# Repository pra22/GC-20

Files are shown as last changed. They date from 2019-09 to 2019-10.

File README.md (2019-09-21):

# GC-20
### Portable Geiger counter, dosimeter and monitoring station with features such as:
- Touchscreen controlled, intuitive GUI
- Displays counts per minute, current dose, and accumulated dose on homescreen
- Sensitive and reliable SBM-20 Geiger-Muller tube
- Variable integration time for averaging dose rate
- Timed count mode for measuring low doses
- Choose between Sieverts and Rems as the units for the displayed dose rate
- User adjustable alert threshold
- Adjustable calibration to relate CPM to dose rate for various isotopes
- Audible clicker and LED indicator toggled on and off from homescreen
- Offline data logging
- Post bulk logged data to cloud service (ThingSpeak) to graph, analyze and/or save to computer
- Monitoring Station mode: device stays connected to WiFi and regularly posts ambient radiation level to ThingSpeak channel

### Overview and User's Guide

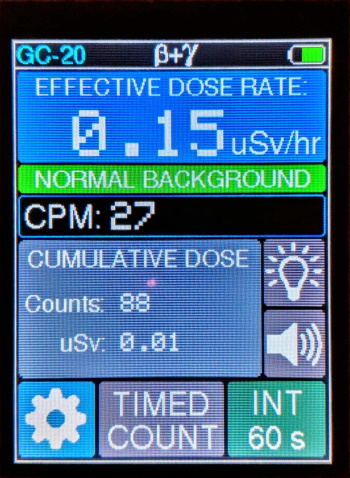
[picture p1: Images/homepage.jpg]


The homepage displays the current effective dose rate, counts per minute, and the cumulative dose since the device was turned on. The integration time can be changed by tapping the "INT 60 s" button and the user can choose between 60, 180 and 5 seconds of integration. A shorter time allows faster response to changing radiation levels at the expense of accuracy. Using 180 seconds gives the least amount random fluctuation.

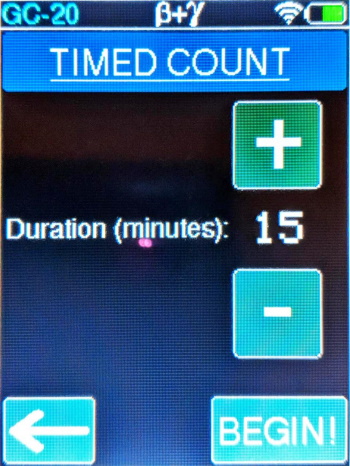
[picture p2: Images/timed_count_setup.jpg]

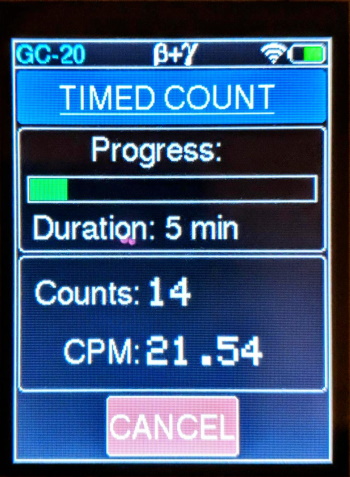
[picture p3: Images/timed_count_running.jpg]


The timed count mode allows for the measurement of very low doses of radiation such as the radiation coming from bananas, brazil nuts, or granite. It can also be used to test for high levels of Radon. Select the time interval in five minute increments, hit begin, and the GC-20 starts counting and displaying the accumulated counts over time. It also displays the real time CPM during the timed count. 
The WiFi symbol next to the battery level indicator means that the GC-20 is currently in monitoring station mode and is connected to WiFi. More on that below.

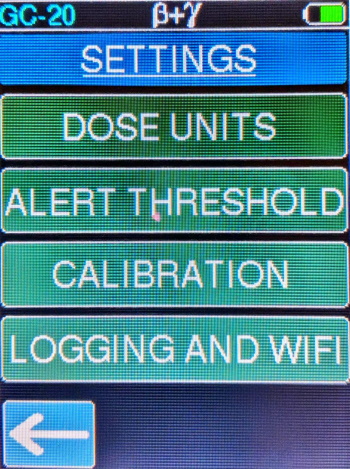
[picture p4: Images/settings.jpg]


The settings menu has four options: Dose Units, Alert Threshold, Calibration, and Logging and WiFi. 

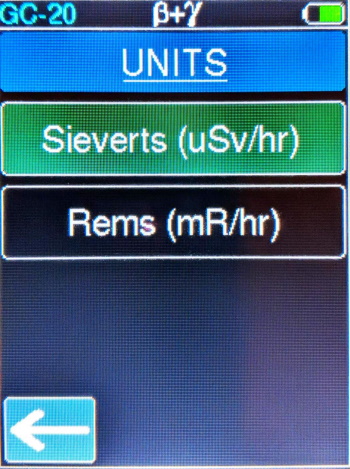
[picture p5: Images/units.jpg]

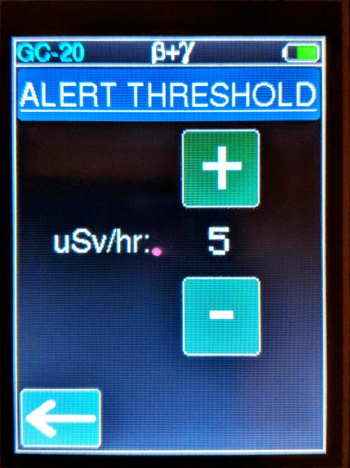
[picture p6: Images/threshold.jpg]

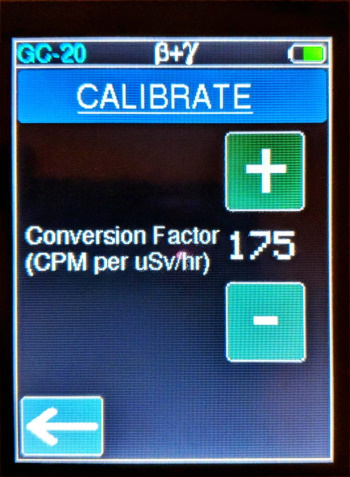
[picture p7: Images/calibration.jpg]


The Dose Units option allows the user to choose between either Sieverts or Rems for the effective dose rate and the accumulated dose.

The user can adjust the threshold at which the home page displays a "High Radiation Level" alert in red, in increments of 1 uSv/hr.

The calibration factor that relates CPM to uSv/hr can be changed using this option. The geiger tube has different sensitivities to different isotopes, so to keep the dose readings reasonably accurate, a default conversion factor of 175 is used. This will accurately report the gamma dose from Cesium-137. 

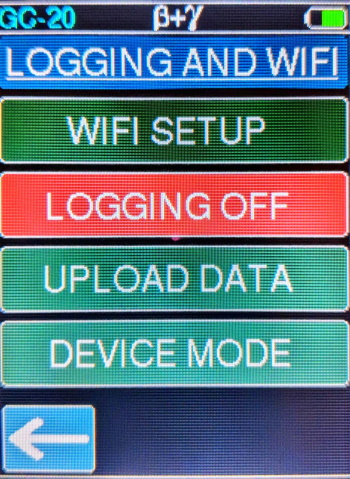
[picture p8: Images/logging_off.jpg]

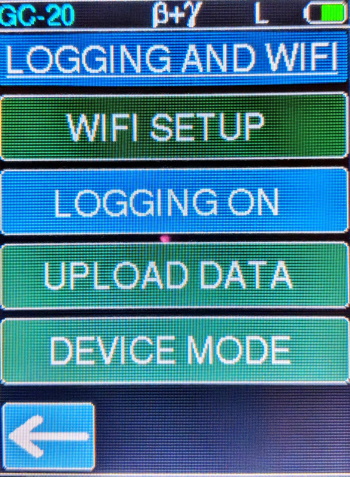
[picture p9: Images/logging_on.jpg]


Finally, tapping the Logging and WiFi button offers a further sub-menu of options related to setting up wifi for the first time, logging data, uploading logged data, and setting the device mode. When data logging is on, an "L" symbol appears on the top bar.

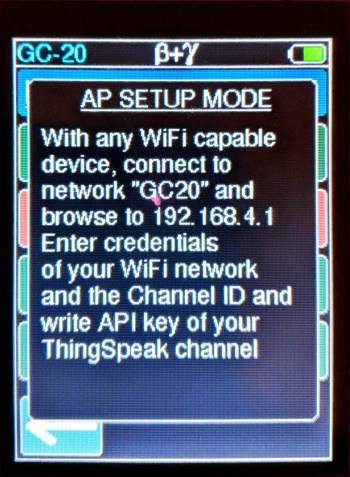
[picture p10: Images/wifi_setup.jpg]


To set up WiFi, tap on WiFi setup and the GC-20 will enter AP mode. Using any wifi connected device with a web browser, like a phone or a laptop, search local networks and connect to the open network named "GC20". The browser will either automatically take you to the setup page, or if doesn't, enter the url 192.168.4.1. Select your network name from the scanned list, enter the password, and also enter the credentials of your ThingSpeak channel, i.e. the channel ID and the write API. Once that's done, hit save and the GC-20 will save the settings to permanent memory and reset itself. You can always change the wifi or channel details at any time by repeating the above.

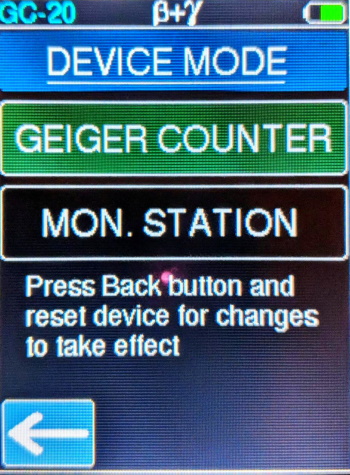
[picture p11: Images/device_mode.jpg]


In the Device Mode menu option, the user can choose between the portable Geiger counter mode, or configure the device as a radiation monitoring station. In the monitoring station mode, the GC-20 is always connected to WiFi, and updates the ThingSpeak field every 5 minutes. If it can't connect to WiFi during startup, it waits for 30 seconds before starting in portable Geiger counter mode.

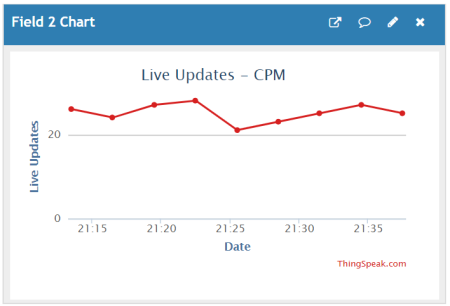
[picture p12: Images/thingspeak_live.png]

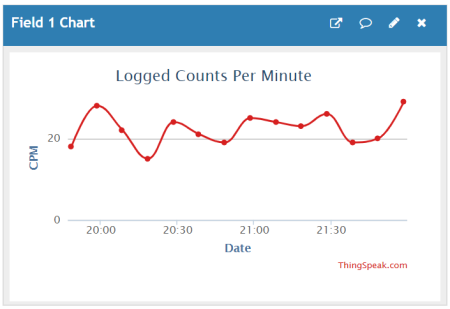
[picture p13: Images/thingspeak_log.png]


Examples of the ThingSpeak data plots from the radiation monitor and from a bulk-upload of logged data.

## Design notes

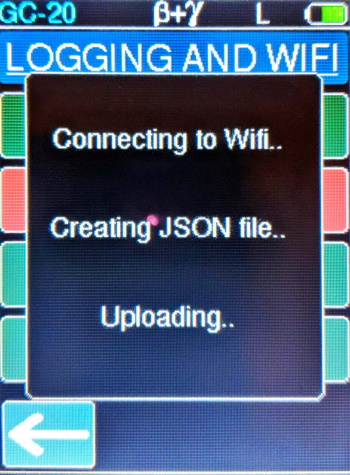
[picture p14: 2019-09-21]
Images/uploading.jpg

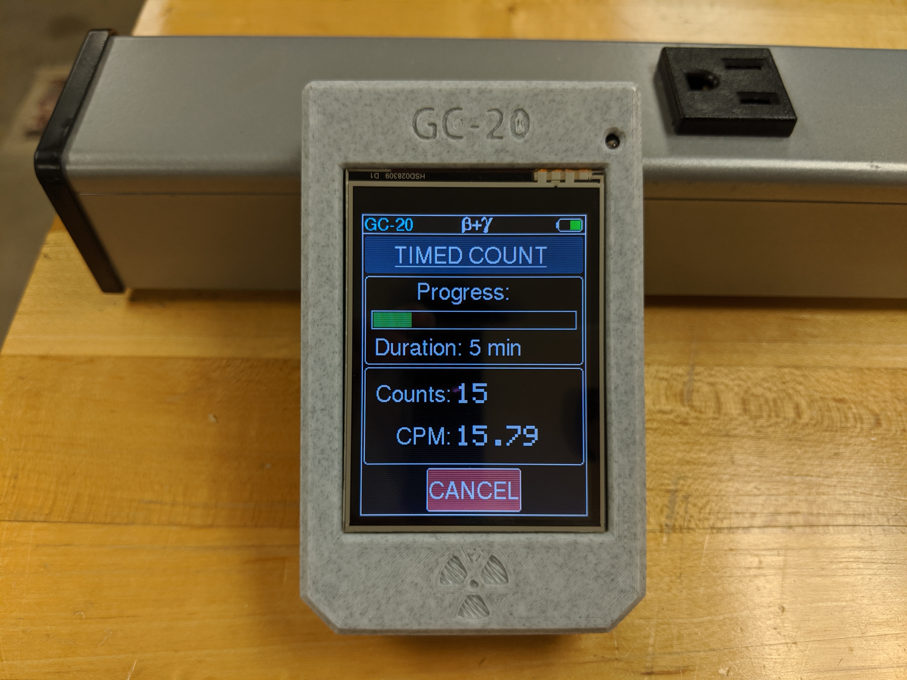
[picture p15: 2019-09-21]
Images/timedcount.jpg

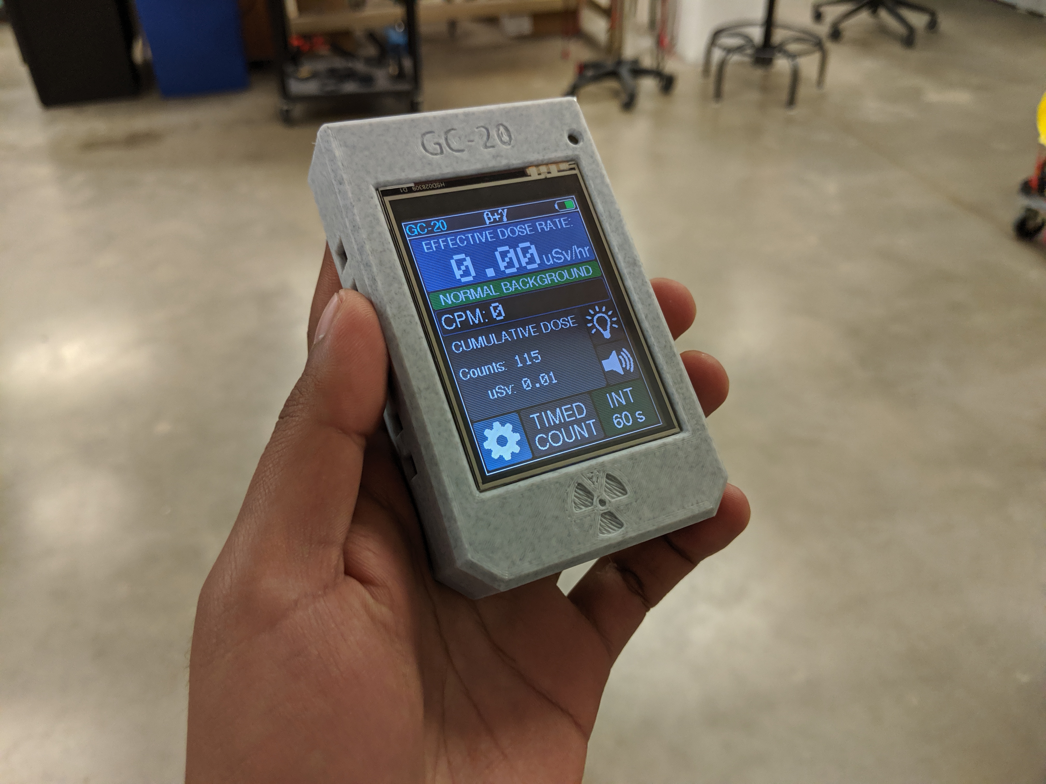
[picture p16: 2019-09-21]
Images/handheld4.jpg

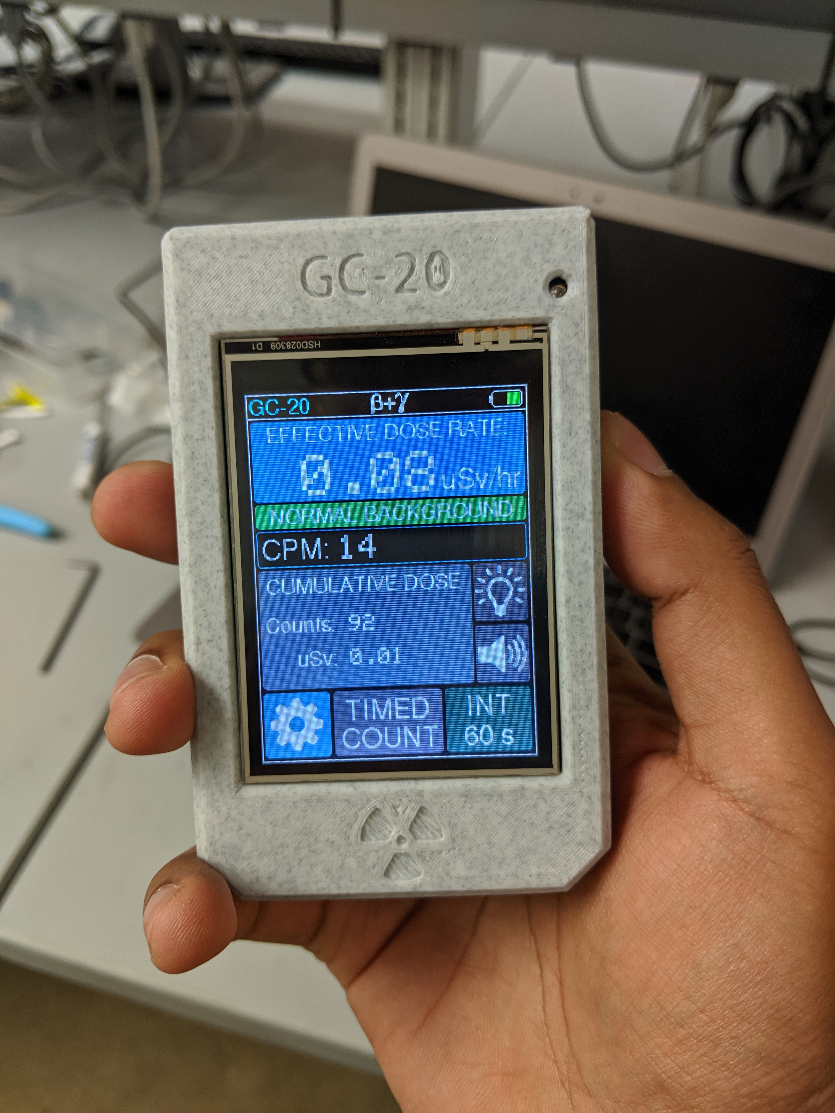
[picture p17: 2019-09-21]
Images/handheld3.jpg

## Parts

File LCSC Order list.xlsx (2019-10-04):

LCSC order information for electronic components for the GC-20
Reference Designator | Value/Description | LCSC Part Number | Footprint
U1 | CMOS 555 timer | C383061 | SOP-8
U5 | 3V LDO linear regulator | C98226 | SOT-89
C1 | 1 nF MLCC 50V | C1885 | 1206
C2 | 10 nF 1000V | C107192 | 1206
C3 | 220 pF MLCC 500V | C106036 | 1206
C4 | 10 uF Tantalum | C119050 | CASE-B_3528
C5 | 100 nF MLCC | C82601 | 1206
R1 | 100K | C17900 | 1206
R2 | 220K | C17956 | 1206
R3 | 330 | C104763 | 1206
R4 | 1K | C4410 | 1206
R5 | 100 Ohm Variable Resistor | C128542 | Custom
R6 | 4.7M | C37800 | 1206
R7 | 10K | C140407 | 1206
R8 | 100K | C17900 | 1206
R9 | 22K | C25830 | 1206
R10 | 220K | C17956 | 1206
R11 | 330 | C104763 | 1206
D1 | Fast recovery 600V diode | C183411 | SMAF
D2 | Fast recovery 600V diode | C183412 | SMAF
Q1 | NPN Transistor 200mA 400V | C181174 | SOT-23
Q2 | NPN Transistor 200mA 40V | C111113 | SOT-23
Q3 | NPN Transistor 200mA 40V | C111113 | SOT-23
Q4 | NPN Transistor 200mA 40V | C111113 | SOT-23
L1 | 10 mH Power Inductor | C168108 | Custom
BUZZER1 | Magnetic Buzzer | C189208 | 7.5*7.5*2.5mm
SW1 | Power switch SMD | C405951 | Custom
B1 | JST PH battery connector | C265016 | TH, 2mm pitch
LED1 | Red LED 3mm | C330752 | TH

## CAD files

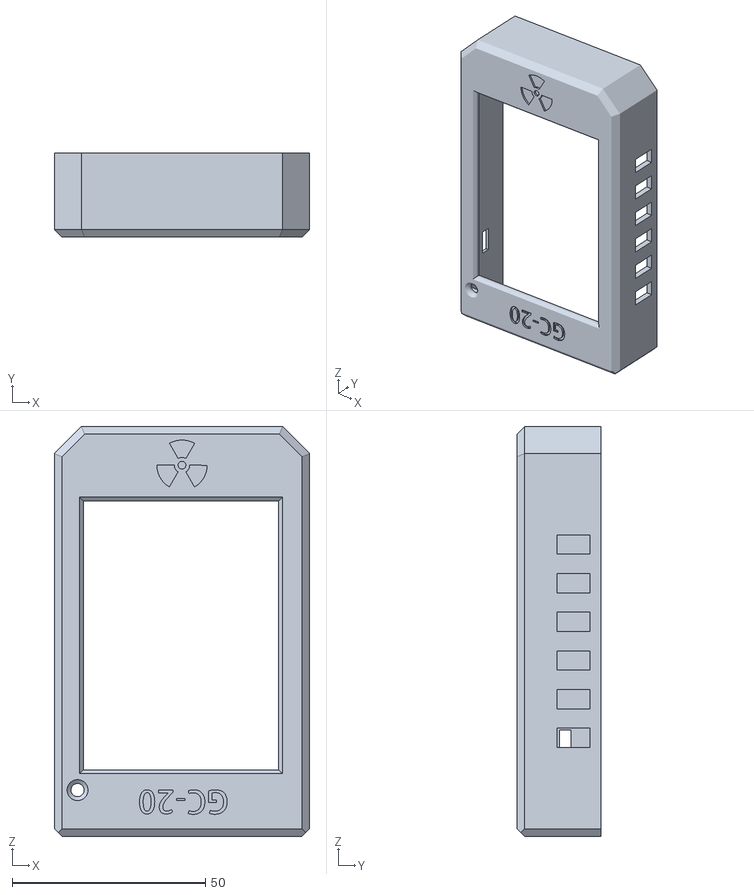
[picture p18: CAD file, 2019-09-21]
STL Files/Case main.STL
66.0 x 21.8 x 106.0

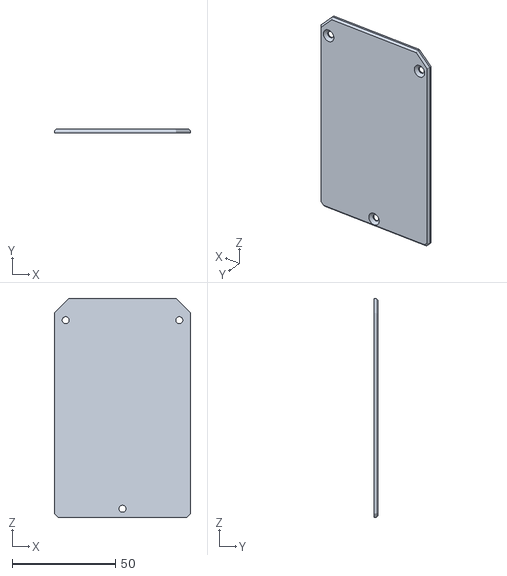
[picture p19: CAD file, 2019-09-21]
STL Files/Cover.STL
66.0 x 2.00 x 106.0

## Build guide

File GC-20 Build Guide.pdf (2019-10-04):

v1.1 | 10/04/2019

### GC-20 Geiger Counter, Dosimeter and Radiation Monitoring Station

Build Guide

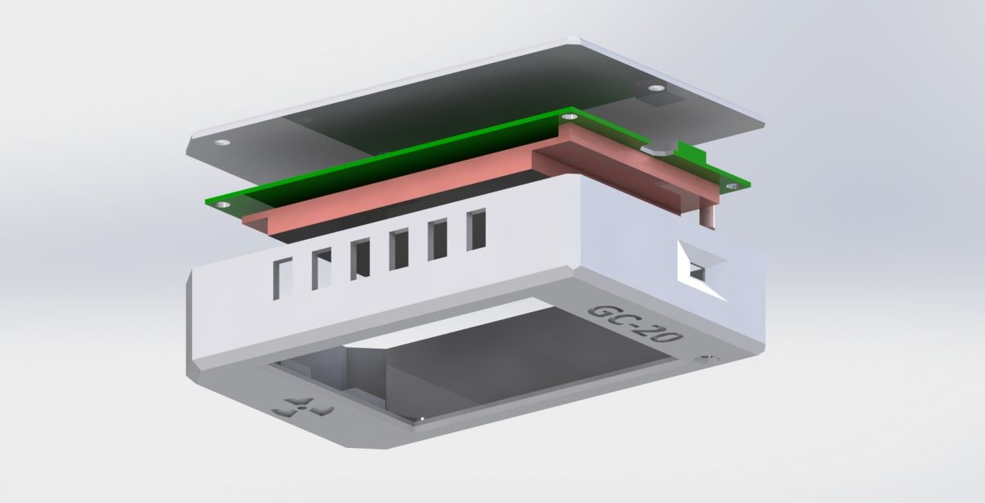
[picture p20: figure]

Figure 1: Rendering of the CAD model

All hardware design files for the GC-20 are available at my GitHub page at github.com/pra22/GC20. This includes the Solidworks CAD assembly, STL files for 3D printing, Gerbers for the PCB, and a PDF schematic of the circuit that contains the part numbers of all electronic components as purchased from LCSC. The passive components are all of size 1206. Most components are SMT, with the exception of the JST connector, LED, D1 Mini, TFT LCD display, the battery charger board, and the connections to the Geiger tube.
The GC-20 uses the Russian SBM-20 Geiger tube. This tube is capable of detecting hard beta and gamma radiation. To keep the size compact, I opted to use the kind with both ends taken off, as shown in the figure below.

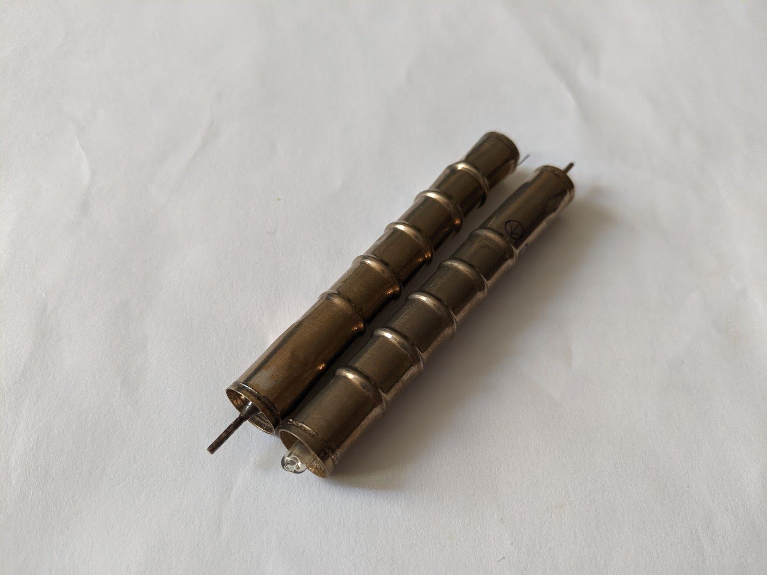
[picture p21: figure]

Figure 2: SBM-20 tubes with exposed leads. The protruding rod is the anode and the tube body is the cathode

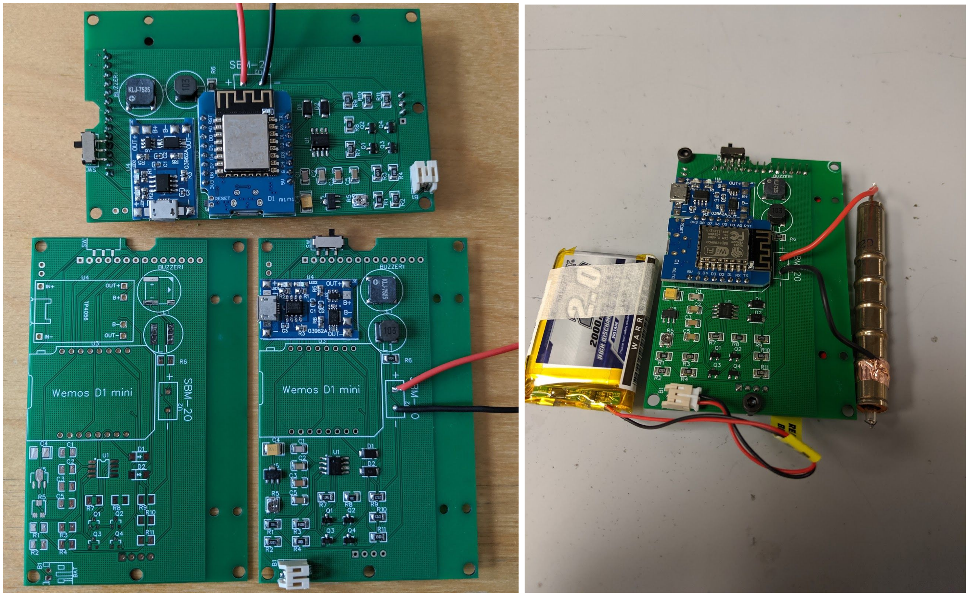
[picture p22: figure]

Figure 3: PCBs at various stages of assembly

I used a toaster oven and a stencil to solder the SMT components and found that this method works well. All parts are labeled and correctly represent the schematic part numbers.

Note: The battery charger board should be soldered like an SMD component by placing it over the pads and flowing solder into the holes. Their hole spacing is odd and won’t fit standard 0.1 in male headers.

The circuit is based on the following schematic diagram:

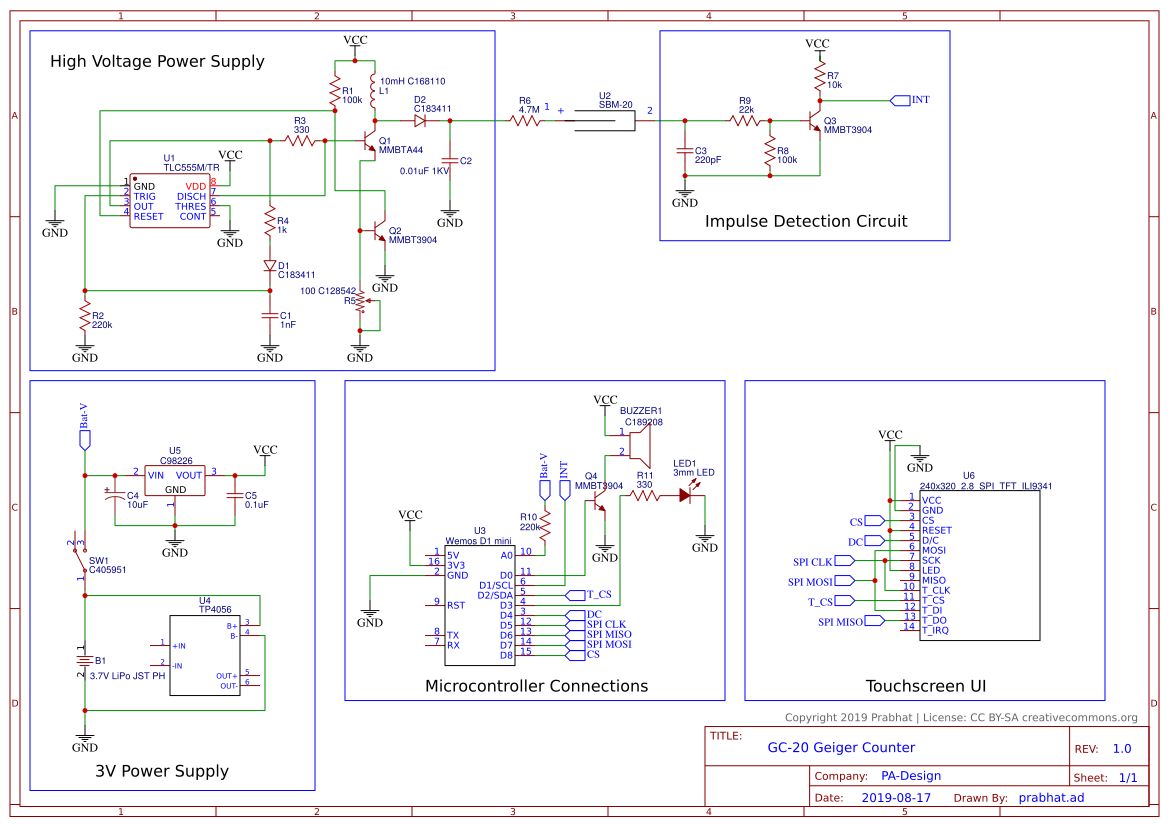
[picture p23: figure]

Figure 4: Complete Circuit Schematic

The part labels for each component in the schematic are either the manufacturer’s part number or the LCSC product number. Find them by searching on LCSC’s website. If you prefer to use a different supplier such as Digikey, the equivalent parts can be found by first reading the product description at LCSC. There are no rare or special components, but I had some trouble finding a 10 mH Ferrite core inductor that worked. The PDF version of this schematic can be found in my GitHub page for a clearer view of the circuit.

The order list from LCSC is as follows:

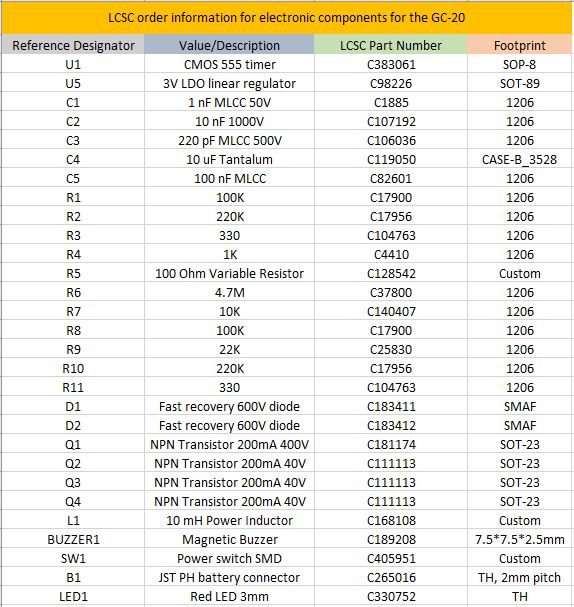
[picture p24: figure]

The following table lists the components used to make the full assembly, NOT including the discrete electronic components to be ordered from LCSC or a similar supplier.

Part Name | Quantity | Link
PCB | 1 | Order from any manufacturer using the Gerber files
Wemos D1 mini | 1 | https://www.amazon.com/IZOKEE-NodeMcu-Internet-Development-Compatible/dp/B076F53B6S/ref=sr_1_5?keywords=D1+mini&qid=1569094374&s=gateway&sr=8-5 (https://www.amazon.com/IZOKEE-NodeMcu-Internet-Development-Compatible/dp/B076F53B6S?s=gateway)
2.8” TFT LCD Touchscreen with SPI interface | 1 | https://www.amazon.com/HiLetgo-240X320-Resolution-Display-ILI9341/dp/B073R7BH1B/ref=sr_1_3?keywords=tft+lcd+touch+spi&qid=1569094450&s= (https://www.amazon.com/HiLetgo-240X320-Resolution-Display-ILI9341/dp/B073R7BH1B?s=gateway)

| | gateway&sr=8-3 (https://www.amazon.com/HiLetgo-240X320-Resolution-Display-ILI9341/dp/B073R7BH1B?s=gateway)
SBM-20 Geiger Tube with ends off | 1 | Many sellers on ebay and other sites. Goes in and out of stock at various online stores.
3.7 V LiPo Charger board | 1 | https://www.amazon.com/Makerfocus-Charging-Lithium-Battery-Protection/dp/B071RG4YWM/ref=sr_1_5?keywords=3.7v+battery+charger+board&qid=1569094608&s=gateway&sr=8-5 (https://www.amazon.com/Makerfocus-Charging-Lithium-Battery-Protection/dp/B071RG4YWM?s=gateway)
Turnigy 3.7V LiPo battery and JST connector | 1 | https://hobbyking.com/en_us/turnigy-2000mah-1s-1 c-lipoly-w-2-pin-jst-ph-connector.html (https://hobbyking.com/en_us/turnigy-2000mah-1s-1c-lipoly-w-2-pin-jst-ph-connector.html)
M3 x 22mm Countersunk screws | 3 | https://www.mcmaster.com/91294a137
M3 x 8mm hex head machine screws | 3 | https://www.amazon.com/M3-0-50-Socket-Stainless-Machine-Quantity/dp/B01L0E1TAY/ref=sr_1_14?keywords=m3+8mm+machine+screws&qid=1569095687&s=gateway&sr=8-14 (https://www.amazon.com/M3-0-50-Socket-Stainless-Machine-Quantity/dp/B01L0E1TAY?s=gateway)
M3 brass threaded insert | 6 | https://www.amazon.com/Uxcell-a16041800ux0824-Knurled-Threaded-Embedment/dp/B01IYWTCWW/ref=sr_1_3?crid=2HA0QXKNMSBWV&keywords=m3+brass+insert&qid=1569095827&s=gateway&sprefix=m3+brass+ins%2Caps%2C151&sr=8-3 (https://www.amazon.com/Uxcell-a16041800ux0824-Knurled-Threaded-Embedment/dp/B01IYWTCWW?s=gateway)
Conductive copper tape | 1 roll | https://www.amazon.com/gp/product/B07R8QBSZ3/ref=ppx_yo_dt_b_asin_title_o01_s00?ie=UTF8&psc=1 (https://www.amazon.com/gp/product/B07R8QBSZ3/ref=ppx_yo_dt_b_asin_title_o01_s00?ie=UTF8&psc=1)

Other miscellaneous parts, equipment and supplies include:

- Soldering Iron
- Hot Air soldering station (optional)
- Toaster Oven for SMD reflow (optional, either do this or the hot air method)
- Solder wire
- Solder paste
- Stencil (optional)
- 3D printer
- PLA filament
- Silicone-insulated stranded wire 22 gauge
- Hex keys

Steps:

1. Solder all SMD components to the PCB first, using your preferred method
2. Solder the battery charger board to the pads SMD-style
3. Solder male leads to the D1 Mini board and to the bottom pads of the LCD board
4. Solder the D1 Mini board to the PCB
5. Cut off all protruding leads from the D1 Mini on the other side
6. Remove the SD card reader from the LCD display. This will interfere with other components on the PCB. A flush cutter works for this
7. Solder through-hole components (JST connector, LED)
8. Solder the LCD board to the PCB AT THE END. You won’t be able to de-solder the D1 Mini after this
9. Cut off the bottom-side protruding male leads from the LCD board on the other side of the PCB
10. Cut two pieces of stranded wire around 8 cm (3 in) long each and strip the ends
11. Solder one of the wires to the anode (rod) of the SBM-20 tube
12. Use the Copper tape to attach the other wire to the body of the SBM-20 tube
13. Tin and solder the other ends of the wires to the through-hole pads on the PCB. Make sure the polarity is correct.
14. Upload the code to the D1 mini with your preferred IDE; I use VS Code with PlatformIO. If you download my GitHub page, it should work without needing any changes
15. Attach the battery to the JST connector and power on to see if it works!
16. 3D print the case and the cover
17. Insert the brass threaded inserts into the six hole locations in the case with a soldering iron
18. Install the assembled PCB to the case and secure with three 8mm screws. Two on top and one on the bottom
19. Place the Geiger tube on the empty side of the PCB (towards the grill) and secure with masking tape.
20. Insert the battery over the top, sitting over the SMD components. Guide the wires to the gap at the bottom of the case. Secure with masking tape.
21. Install the back cover using three M3 x 22 mm countersunk screws. Done!

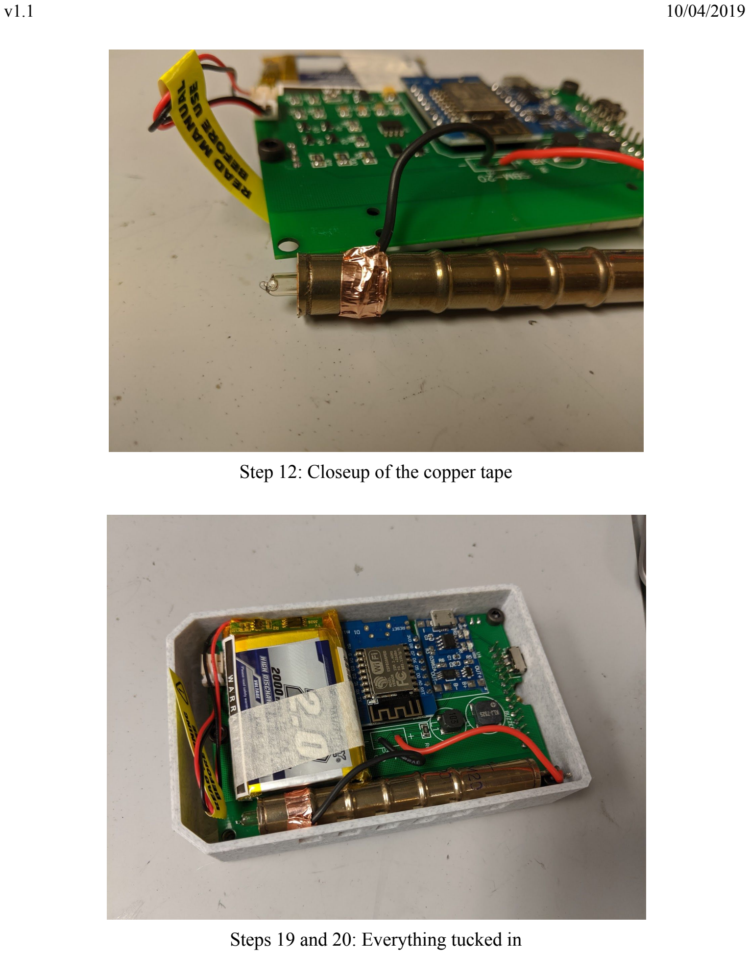
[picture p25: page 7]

Step 12: Closeup of the copper tape

Steps 19 and 20: Everything tucked in

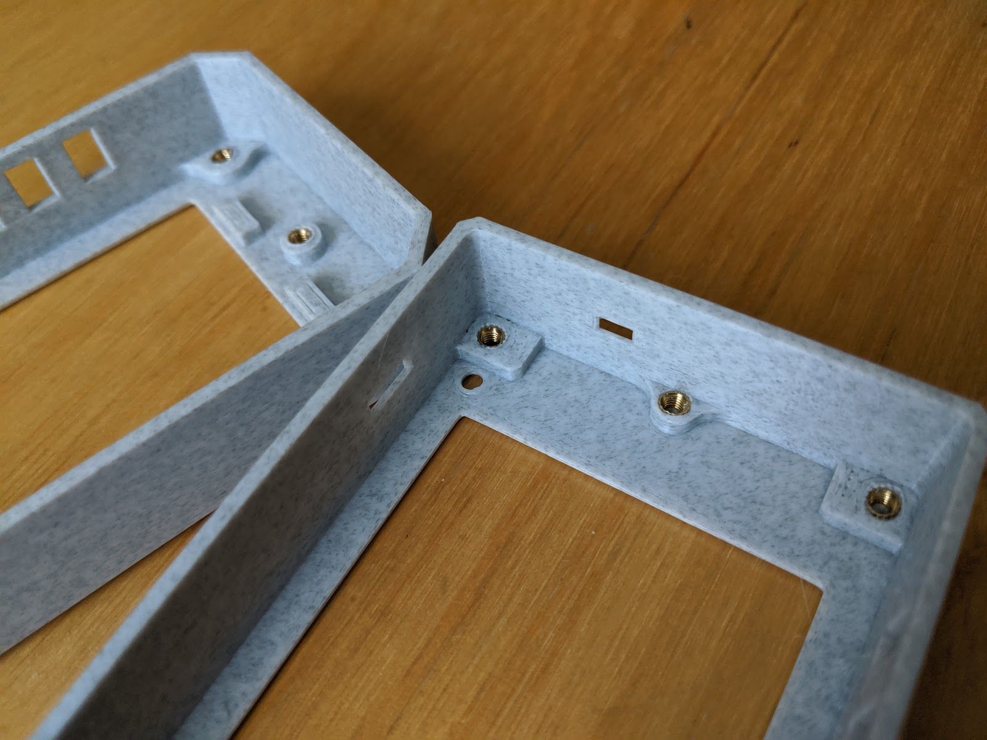
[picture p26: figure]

Step 17: Brass inserts soldered into holes

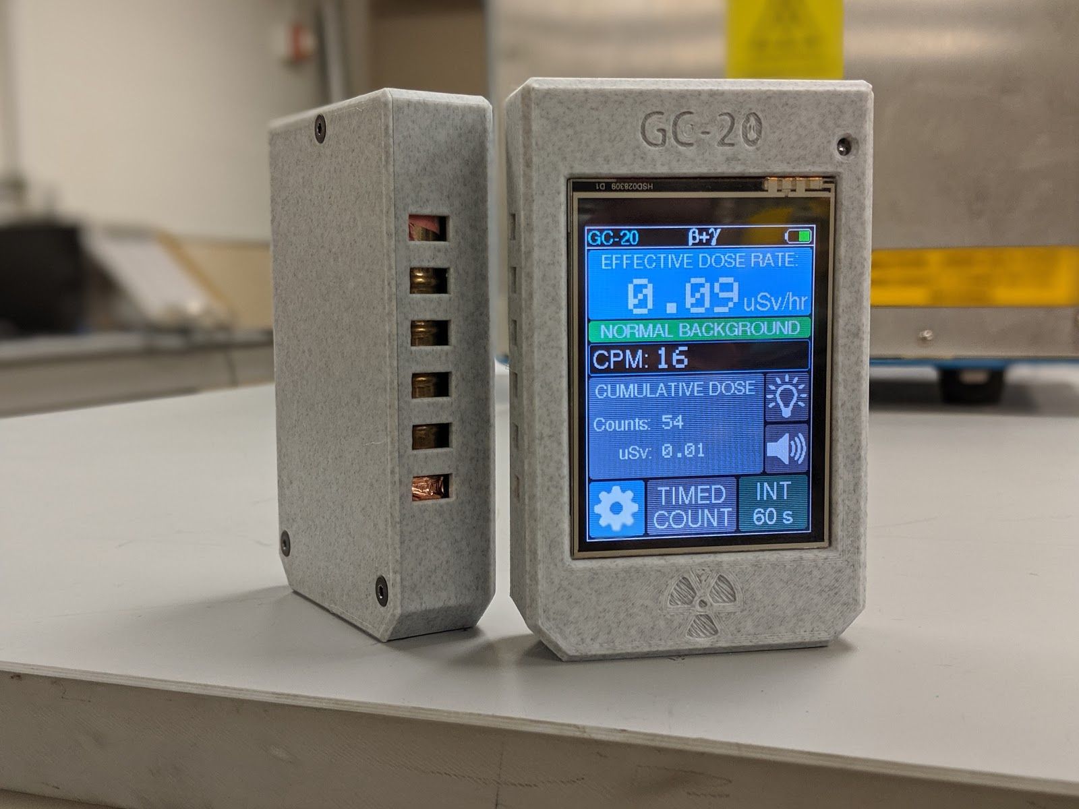
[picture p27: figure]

The result!

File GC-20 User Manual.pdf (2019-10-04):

v1.1 | 10/04/2019

### GC-20 Geiger Counter, Dosimeter and Radiation Monitoring Station

### User Manual


Overview of Hardware

Housing:
The case of the GC-20 is 3D printed from PLA. It is designed to be compact and strong enough to withstand normal use including vibrations or low drops. If your GC-20’s housing is damaged, the STL files to 3D print a new one are available on my GitHub page at github.com/pra22/GC20.

The PCB is secured to the housing with the help of three M3 machine screws that thread into brass inserts, providing a strong, metal-to-metal fastening. Repeated disassembly and reassembly won’t wear out the threads easily. The back cover is installed using M3 countersunk screws into the same kind of brass threaded inserts.

Electronics:
The GC-20 has a high voltage generation circuit that produces the 400V needed by the SBM-20 Geiger-Muller tube. The circuit is based on a 555 oscillator and an inductor whose output is rectified and smoothed out to generate a constant output voltage.

A D1 Mini microcontroller board functions as the brains of the GC-20. This board is based on the ESP8266 chip by Espressif, and comes with WiFi built-in. All electronic components are soldered onto the main PCB.

CAUTION: THIS DEVICE USES HIGH VOLTAGE. DISASSEMBLY SHOULD BE CARRIED OUT WITH CARE, AND IMPROPER HANDLING CAN CAUSE A MILD (BUT ANNOYING) SHOCK

Power:
Power is provided by a 3.7V Lithium-Ion Polymer battery with a capacity of 2000 mAh. The battery is rechargeable with a standard micro-USB charging port on the side on the GC-20. The GC-20 consumes an average of 120 mA during normal use without WiFi, giving a battery life of around 16 hours.
A standard wall USB charger can be used to charge the battery. The power system comes with overcharge, overdischarge, and short circuit protection.

Note: Please make sure that the charger can provide at least 1 A of current at 5 V. Using a lower current (such as the USB port on a computer) might not charge the battery properly.

The battery is connected to the PCB with a standard JST-PH connector with a 2mm pitch. The battery can be easily removed by taking off the back cover, making it possible to carry multiple batteries if a longer runtime is needed and charging is not available.

Software Features Summary

The GC-20 comes with a clean, intuitive user interface with touch controls for ease of use and quick access to all functions. No more navigating clunky, complicated menus with limited input options. The following is a rundown of the major software features that the GC-20 offers.

Home screen:

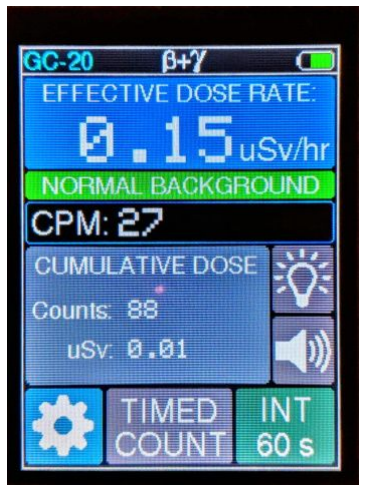
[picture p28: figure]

Figure 1: The home screen of the GC-20

The home screen displays the current effective dose rate, counts per minute, and the cumulative dose since the device was turned on. The integration time can be changed by tapping the "INT 60 s" button and the user can choose between 60, 180 and 5 seconds of integration. A shorter time allows a faster response to changing radiation levels at the expense of accuracy. It is useful when measuring higher levels of radiation and a quick response to changing radiation levels is desired. Using 180 seconds results in the least amount of random fluctuation, and is useful for monitoring natural background levels.
The light bulb and speaker buttons can be used to toggle the indicator LED and the buzzer on or off respectively.
The battery level indicator shows the current charge state of the battery. The level indicator will turn red from green if the battery is under 10% of its capacity.

Timed Count Mode:

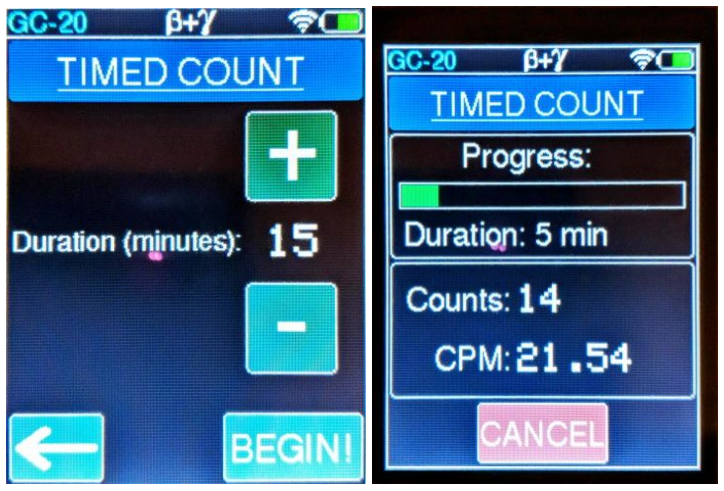
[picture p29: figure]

Figure 2: Timed count setup and running displays

The timed count mode allows for the measurement of low doses of radiation such as the radiation coming from bananas, brazil nuts, or granite. It can also be used to test for high levels of Radon. Select the time interval in five minute increments, hit begin, and the GC-20 starts counting and displaying the accumulated counts over time. It also displays the real time CPM during the timed count. By doing a similar timed count of the natural background, the user can compare and detect small differences in radiation levels.
The WiFi symbol next to the battery level indicator means that the GC-20 is currently in monitoring station mode and is connected to WiFi. More on that below.

Settings:

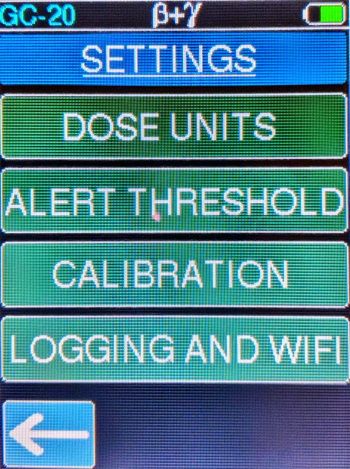
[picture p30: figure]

Figure 3: Settings page

The settings menu has four options: Dose Units, Alert Threshold, Calibration, and Logging and WiFi.

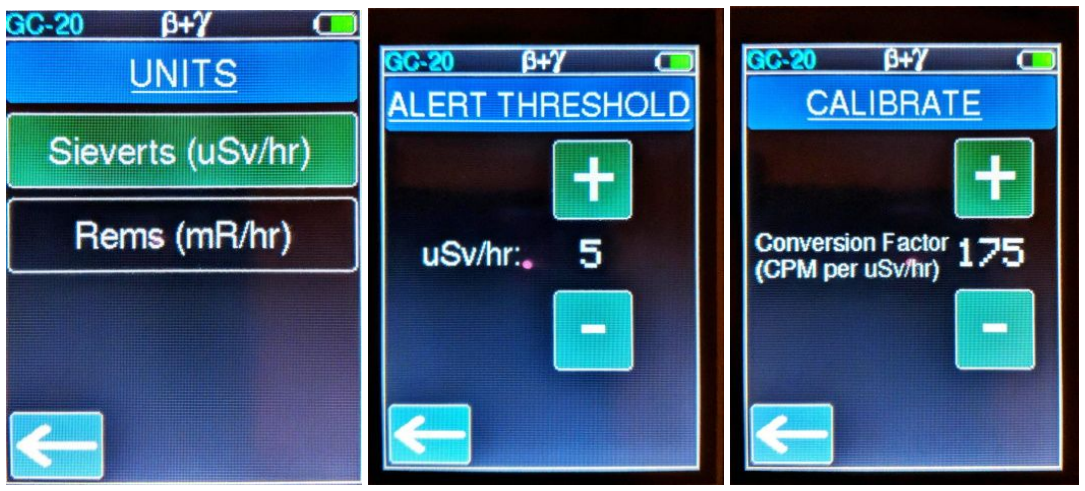
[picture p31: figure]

Figure 4: The first three settings options

The Dose Units option allows the user to choose between either Sieverts or Rems for the effective dose rate and the accumulated dose.

The user can adjust the threshold at which the home page displays a "High Radiation Level" alert in red, in increments of 1 uSv/hr.

The calibration factor that relates CPM to uSv/hr can be changed using this option. The geiger tube has different sensitivities to different isotopes, so to keep the dose readings reasonably accurate, a default conversion factor of 175 is used. This will accurately report the gamma dose from Cesium-137.

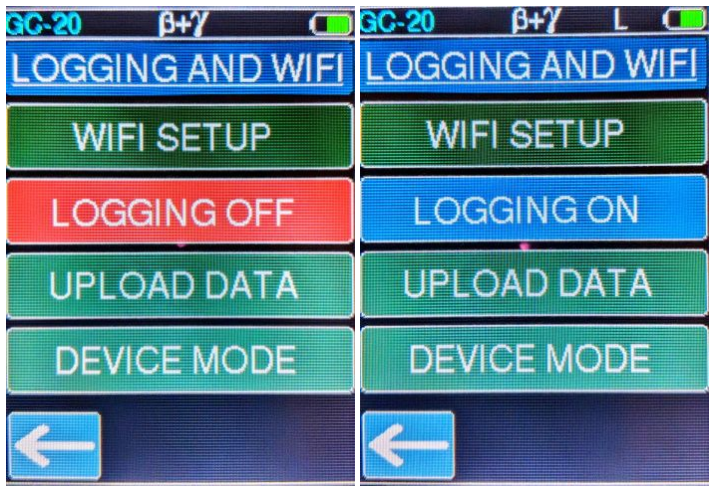
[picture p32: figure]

Figure 5: Logging and Wifi setup page with additional options

Finally, tapping the Logging and WiFi button offers a further sub-menu of options related to setting up wifi for the first time, logging data, uploading logged data, and setting the device mode. When data logging is on, an "L" symbol appears on the top bar and the GC-20 begins logging the counts per minute once every 10 minutes. The GC-20 can store upto 150 hours of logs before the memory is full, which is indicated by a “Log Memory Full” message in the page displayed above.
Resetting the device won’t erase any logged data since it is stored in permanent memory. The GC-20 will continue logging where it left off when powered up again.
Note: Since the GC-20 doesn’t come with a built-in clock, the logged data will contain relative timestamps of 10 minutes.

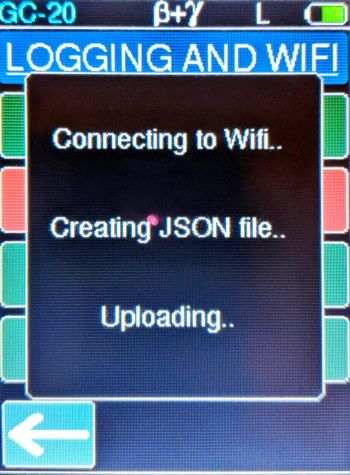
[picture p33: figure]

Figure 6: Uploading logged data to ThingSpeak

By tapping the “Upload Data” button, the user can bulk-upload the logged data to their ThingSpeak channel. The uploaded data will populate “Field 1” of the channel. If the data is successfully uploaded, the GC-20 will clear all logs and reset itself.

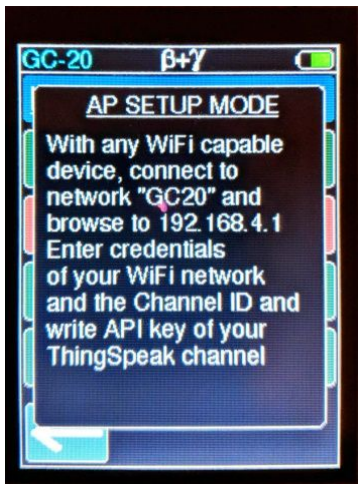
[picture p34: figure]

Figure 7: WiFi setup mode.

Before setting up WiFi, create a new free account on ThingSpeak, add a new channel, and find the Channel ID and the Write API Key for the channel.

To use the WiFi features of the GC-20, such as uploading logs and using the device as a radiation monitoring station, the user first needs to set up the WiFi and enter the credentials of their ThingSpeak channel. To do this, tap on the “WiFi Setup” button and the GC-20 will enter Access Point mode. Using any wifi capable device with a web browser, like a phone or a laptop, search local networks and connect to the open network named "GC20". The browser will either automatically take you to the setup page, or if doesn't, enter the url 192.168.4.1. Select your network name from the scanned list or enter the SSID (network name) manually, enter the password, and also enter the credentials of your ThingSpeak channel, i.e. the channel ID and the Write API Key. Once that's done, hit save and the GC-20 will save the settings to permanent memory and reset itself. This only needs to be done once. You can always change the WiFi or channel details at any time by repeating the above.

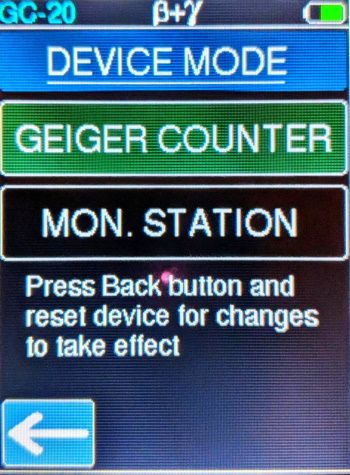
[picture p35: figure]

Figure 8: Device mode selection menu

In the Device Mode menu option, the user can choose between the portable Geiger counter mode, or configure the device as a radiation monitoring station. In the monitoring station mode, the GC-20 is always connected to WiFi, and updates the ThingSpeak field every 5 minutes. The uploaded data will populate “Field 2” of the ThingSpeak channel. If it can't connect to WiFi during startup, it waits for 30 seconds before starting in portable Geiger counter mode. In monitoring station mode, the recommended integration time is 180 seconds.

Note: When using the GC-20 as a radiation monitoring station, it is recommended to remove the battery and keep it plugged in to a USB outlet. The top screw in the back can be removed and the hole can be used for mounting the device onto a nail on a wall. If the device is to be stationed outdoors, please use an enclosure that prevents excessive moisture from getting in. To prevent softening of the case in hot weather, the case can be removed and the bare device can be kept in a separate enclosure.

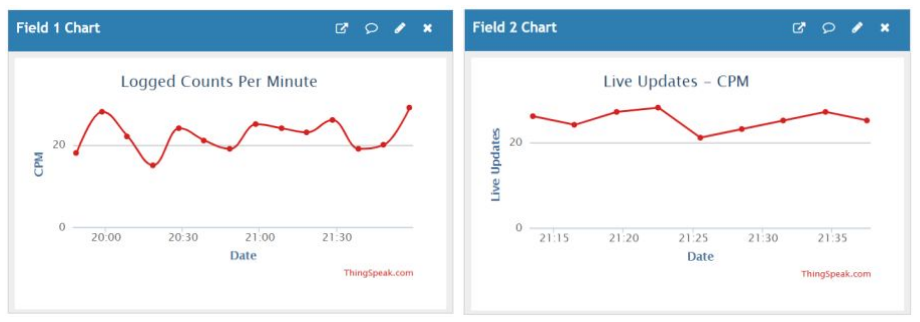
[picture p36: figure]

Figure 9: Examples of ThingSpeak data plots for logged data (left) and live upload (right)

The ThingSpeak channel allows the user to customize the appearance of the graphs, change the axis labels, data min and max values, number of data points to display, etc among other options. The user also has the option to save the uploaded data as JSON, XML or CSV (Excel compatible) files.

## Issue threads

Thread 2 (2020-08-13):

### ISSUE TITLE
platformio libraries

### ISSUE THREAD

**Issue by pizvizdik** [pra22/GC-20#2]
hi, i am getting error during compilation in platformio:

src/main.cpp:13:25: fatal error: WifiManager.h: No such file or directory

i tried to reinstall libraries (wifimanager) but no luck.. any ideas what is causing this error?

thank you..

**Comment by manuelchaves** [comment]
Hi, in src/main.ccp include this line:

#include <Wire.h>

**Comment by pizvizdik** [comment]
already tried that, still getting same err.. but funny thing - error only shows under linux (pop OS), in windows everything seems to be OK, upload seems finished but nothing on display:

src/main.cpp:13:25: fatal error: WifiManager.h: No such file or directory

*********************************************************************
* Looking for WifiManager.h dependency? Check our library registry!
*
* CLI  > platformio lib search "header:WifiManager.h"
* Web  > https://platformio.org/lib/search?query=header:WifiManager.h
*
*********************************************************************

 #include <WifiManager.h>
                         ^
compilation terminated.
Compiling .pio/build/nodemcuv2/lib9f2/ESP8266WiFi/ESP8266WiFiSTA-WPS.cpp.o
Compiling .pio/build/nodemcuv2/lib9f2/ESP8266WiFi/ESP8266WiFiSTA.cpp.o
Compiling .pio/build/nodemcuv2/lib9f2/ESP8266WiFi/ESP8266WiFiScan.cpp.o
Compiling .pio/build/nodemcuv2/lib9f2/ESP8266WiFi/WiFiClient.cpp.o
Compiling .pio/build/nodemcuv2/lib9f2/ESP8266WiFi/WiFiClientSecureAxTLS.cpp.o
Compiling .pio/build/nodemcuv2/lib9f2/ESP8266WiFi/WiFiClientSecureBearSSL.cpp.o
Compiling .pio/build/nodemcuv2/lib9f2/ESP8266WiFi/WiFiServer.cpp.o
*** [.pio/build/nodemcuv2/src/main.cpp.o] Error 1

**Comment by pizvizdik** [comment]
tried to reinstall linux (pop os) with fresh installation of visual code, but still getting error:

src/main.cpp:13:25: fatal error: WifiManager.h: No such file or directory

*********************************************************************
* Looking for WifiManager.h dependency? Check our library registry!
*
* CLI  > platformio lib search "header:WifiManager.h"
* Web  > https://platformio.org/lib/search?query=header:WifiManager.h
*
*********************************************************************

 #include <WifiManager.h>
                         ^
compilation terminated.
Indexing .pio/build/nodemcuv2/lib052/libAdafruit GFX Library_ID13.a
Compiling .pio/build/nodemcuv2/libb9f/Adafruit STMPE610_ID377/Adafruit_STMPE610.cpp.o
Compiling .pio/build/nodemcuv2/libc4a/Adafruit TouchScreen_ID5430/TouchScreen.cpp.o
Compiling .pio/build/nodemcuv2/lib4a5/Adafruit ILI9341_ID571/Adafruit_ILI9341.cpp.o
Compiling .pio/build/nodemcuv2/libb5b/XPT2046_Touchscreen_ID542/XPT2046_Touchscreen.cpp.o
*** [.pio/build/nodemcuv2/src/main.cpp.o] Error 1
================================================================================= [FAILED] Took 1.94 seconds =================================================================================
The terminal process terminated with exit code: 1

**Comment by Pusmos** [comment]
Hi, I am having problems with uploading the code aswell. I am very new to using PlatformIO or anything for that matter and I am hoping someone would be so kind and help me fix this Issue. I downloaded the Github Page, Installed VS Code and PlatformIO, plugged in the D1 Mini and opened the .ini file and then clicked Upload. This is what I keep getting: (Sorry for the long text) 

> Executing task: C:\Users\Raphael.Catchpole\.platformio\penv\Scripts\platformio.exe run --target upload <

Processing nodemcuv2 (platform: espressif8266; board: nodemcuv2; framework: arduino)
----------------------------------------------------------------------------------------------------------
Verbose mode can be enabled via `-v, --verbose` option
CONFIGURATION: https://docs.platformio.org/page/boards/espressif8266/nodemcuv2.html
PLATFORM: Espressif 8266 2.5.3 > NodeMCU 1.0 (ESP-12E Module)
HARDWARE: ESP8266 160MHz, 80KB RAM, 4MB Flash
PACKAGES:
 - framework-arduinoespressif8266 3.20701.0 (2.7.1)
 - tool-esptool 1.413.0 (4.13)
 - tool-esptoolpy 1.20800.0 (2.8.0)
 - tool-mkspiffs 1.200.0 (2.0)
 - toolchain-xtensa 2.40802.200502 (4.8.2)
LDF: Library Dependency Finder -> http://bit.ly/configure-pio-ldf
LDF Modes: Finder ~ chain, Compatibility ~ soft
Found 36 compatible libraries
Scanning dependencies...
Dependency Graph
|-- <Adafruit GFX Library> 1.9.0
|   |-- <Adafruit BusIO> 1.3.3
|   |   |-- <SPI> 1.0
|   |-- <SPI> 1.0
|-- <Adafruit ILI9341> 1.5.5
|   |-- <Adafruit GFX Library> 1.9.0
|   |   |-- <Adafruit BusIO> 1.3.3
|   |   |   |-- <SPI> 1.0
|   |   |-- <SPI> 1.0
|   |-- <Adafruit STMPE610> 1.1.2
|   |   |-- <SPI> 1.0
|   |-- <Adafruit TouchScreen> 1.1.0
|   |-- <SPI> 1.0
|-- <XPT2046_Touchscreen> 0.0.0-alpha+sha.26b691b2c8
|   |-- <SPI> 1.0
|-- <WifiManager> 0.15.0
|   |-- <DNSServer> 1.1.1
|   |   |-- <ESP8266WiFi> 1.0
|   |-- <ESP8266WebServer> 1.0
|   |   |-- <ESP8266WiFi> 1.0
|   |-- <ESP8266WiFi> 1.0
|-- <SPI> 1.0
|-- <DNSServer> 1.1.1
|   |-- <ESP8266WiFi> 1.0
|-- <EEPROM> 1.0
|-- <ESP8266WebServer> 1.0
|   |-- <ESP8266WiFi> 1.0
|-- <ESP8266WiFi> 1.0
|-- <Ethernet(esp8266)> 1.0.4
|   |-- <SPI> 1.0
Building in release mode
Compiling .pio\build\nodemcuv2\libe52\Adafruit BusIO_ID6214\Adafruit_BusIO_Register.cpp.o
Compiling .pio\build\nodemcuv2\libe52\Adafruit BusIO_ID6214\Adafruit_I2CDevice.cpp.o
Compiling .pio\build\nodemcuv2\libb21\Adafruit GFX Library_ID13\Adafruit_MonoOLED.cpp.o
Compiling .pio\build\nodemcuv2\lib217\Adafruit STMPE610_ID377\Adafruit_STMPE610.cpp.o
In file included from .pio\libdeps\nodemcuv2\Adafruit BusIO_ID6214/Adafruit_BusIO_Register.h:1:0,
                 from .pio\libdeps\nodemcuv2\Adafruit BusIO_ID6214\Adafruit_BusIO_Register.cpp:1:
.pio\libdeps\nodemcuv2\Adafruit BusIO_ID6214/Adafruit_I2CDevice.h:1:18: fatal error: Wire.h: No such file
or directory

**************************************************************
* Looking for Wire.h dependency? Check our library registry!
*
* CLI  > platformio lib search "header:Wire.h"
* Web  > https://platformio.org/lib/search?query=header:Wire.h
*
**************************************************************

 #include <Wire.h>
                  ^
compilation terminated.
*** [.pio\build\nodemcuv2\libe52\Adafruit BusIO_ID6214\Adafruit_BusIO_Register.cpp.o] Error 1
In file included from .pio\libdeps\nodemcuv2\Adafruit BusIO_ID6214\Adafruit_I2CDevice.cpp:1:0:
.pio\libdeps\nodemcuv2\Adafruit BusIO_ID6214/Adafruit_I2CDevice.h:1:18: fatal error: Wire.h: No such file
or directory

**************************************************************
* Looking for Wire.h dependency? Check our library registry!
*
* CLI  > platformio lib search "header:Wire.h"
* Web  > https://platformio.org/lib/search?query=header:Wire.h
*
**************************************************************

 #include <Wire.h>
                  ^
compilation terminated.
*** [.pio\build\nodemcuv2\libe52\Adafruit BusIO_ID6214\Adafruit_I2CDevice.cpp.o] Error 1
In file included from .pio\libdeps\nodemcuv2\Adafruit GFX Library_ID13\Adafruit_MonoOLED.h:30:0,
                 from .pio\libdeps\nodemcuv2\Adafruit GFX Library_ID13\Adafruit_MonoOLED.cpp:20:
.pio\libdeps\nodemcuv2\Adafruit BusIO_ID6214/Adafruit_I2CDevice.h:1:18: fatal error: Wire.h: No such file
or directory

**************************************************************
* Looking for Wire.h dependency? Check our library registry!
*
* CLI  > platformio lib search "header:Wire.h"
* Web  > https://platformio.org/lib/search?query=header:Wire.h
*
**************************************************************

 #include <Wire.h>
                  ^
compilation terminated.
*** [.pio\build\nodemcuv2\libb21\Adafruit GFX Library_ID13\Adafruit_MonoOLED.cpp.o] Error 1
.pio\libdeps\nodemcuv2\Adafruit STMPE610_ID377\Adafruit_STMPE610.cpp:32:18: fatal error: Wire.h: No such file or directory

**************************************************************
* Looking for Wire.h dependency? Check our library registry!
*
* CLI  > platformio lib search "header:Wire.h"
* Web  > https://platformio.org/lib/search?query=header:Wire.h
*
**************************************************************

 #include <Wire.h>
                  ^
compilation terminated.
*** [.pio\build\nodemcuv2\lib217\Adafruit STMPE610_ID377\Adafruit_STMPE610.cpp.o] Error 1
======================================= [FAILED] Took 5.33 seconds =======================================
The terminal process terminated with exit code: 1

Terminal will be reused by tasks, press any key to close it.

**Comment by pizvizdik** [comment]
SOLVED!!! :3
it was problem with my windows PC, after fresh install my code is uploaded to esp, sweet :)

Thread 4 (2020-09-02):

### ISSUE TITLE
voltage problem

### ISSUE THREAD

**Issue by pizvizdik** [pra22/GC-20#4]
sorry for starting this new thread..

i have now problem with voltage, max output i am getting for tube is around 280V.. i checked every component before soldering it to the board and to be sure, tried to make a new board with fresh components - no progress..
could be trimmer the one to blame?

thank you, for your time..

**Comment by wlianmin** [comment]
> sorry for starting this new thread..
> 
> i have now problem with voltage, max output i am getting for tube is around 280V.. i checked every component before soldering it to the board and to be sure, tried to make a new board with fresh components - no progress..
> could be trimmer the one to blame?
> 
> thank you, for your time..

The internal resistance of a voltage meter is around 10MΩ。
So the actual voltage on the tube  should be 411.6V（tube‘s internal resistance ≈ ∞）
![2](https://user-images.githubusercontent.com/7938525/91027134-40e73600-e62e-11ea-817e-56a63f4ae318.png)

**Comment by pizvizdik** [comment]
my mistake.. thank you very much for explaining :) device is working like a charm :3

**Comment by aminhusni** [comment]
> > sorry for starting this new thread..
> > i have now problem with voltage, max output i am getting for tube is around 280V.. i checked every component before soldering it to the board and to be sure, tried to make a new board with fresh components - no progress..
> > could be trimmer the one to blame?
> > thank you, for your time..
> 
> The internal resistance of a voltage meter is around 10MΩ。 So the actual voltage on the tube should be 411.6V（tube‘s internal resistance ≈ ∞） ![2](https://user-images.githubusercontent.com/7938525/91027134-40e73600-e62e-11ea-817e-56a63f4ae318.png)

Won't that mean the voltage drop across the tube is only 280v? The tube's recommended working voltage is still 350 volts - 475 volts.

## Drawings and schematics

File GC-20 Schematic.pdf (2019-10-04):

## High Voltage Power Supply

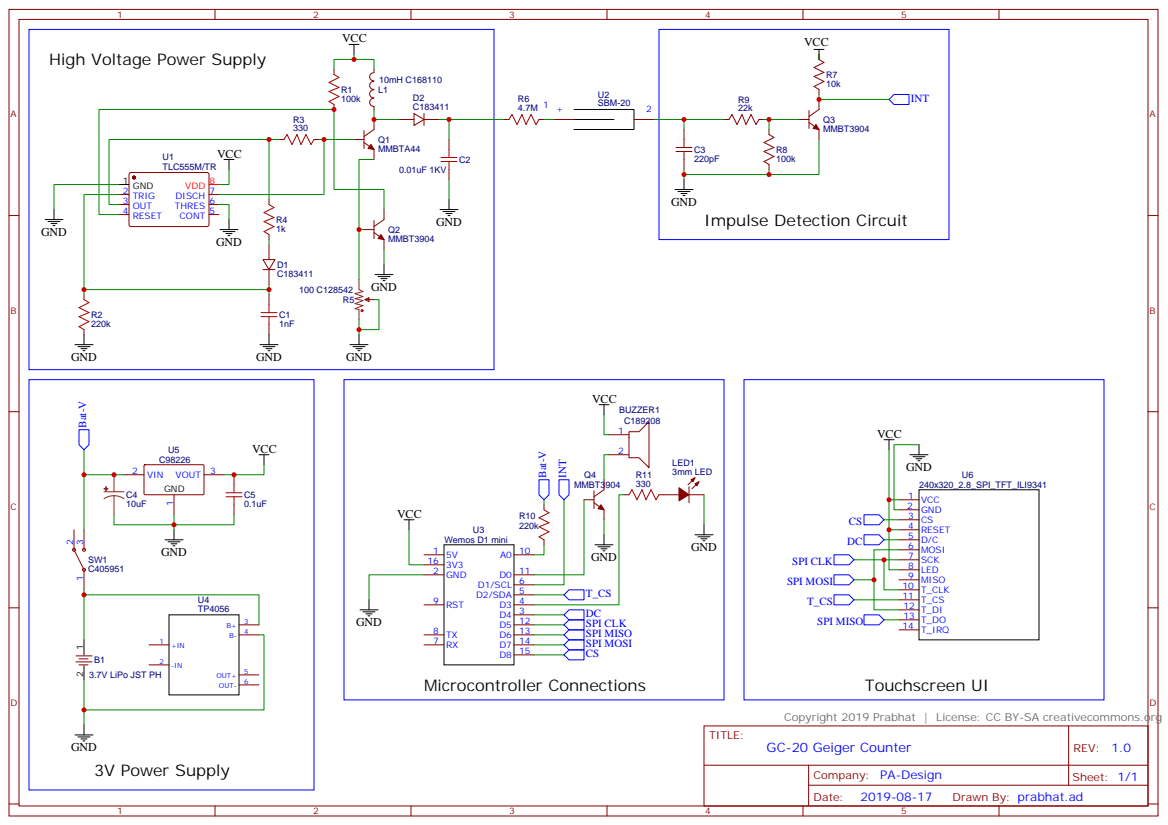
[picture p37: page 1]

Copyright 2019 Prabhat | License: CC BY-SA creativecommons.org

Drawn By: prabhat.ad

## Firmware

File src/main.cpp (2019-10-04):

/*  SBM-20 based Geiger Counter
    Author: Prabhat    Email: pra22@pitt.edu
    Sketch for ESP8266 that counts clicks from the Geiger tube, calculates the counts per minute, and displays information 
    on a TFT touchscreen.
    Attribution-ShareAlike 4.0 International (CC BY-SA 4.0)
*/
#include <Arduino.h>
#include <ESP8266WiFi.h>
#include <EthernetClient.h>
#include <DNSServer.h>
#include <ESP8266WebServer.h>
#include <WifiManager.h>
#include <EEPROM.h>
#include "SPI.h"
#include "Adafruit_GFX.h"
#include <Fonts/FreeSans9pt7b.h>
#include <Fonts/FreeSans12pt7b.h>
#include "Adafruit_ILI9341.h"
#include <XPT2046_Touchscreen.h>

#define CS_PIN D2
XPT2046_Touchscreen ts(CS_PIN);

#define TS_MINX 250
#define TS_MINY 200 // calibration points for touchscreen
#define TS_MAXX 3800
#define TS_MAXY 3750

#define TFT_DC D4
#define TFT_CS D8

#define BLACK 0x0000
#define BLUE 0x001F
#define RED 0xF800
#define GREEN 0x07E0
#define CYAN 0x07FF
#define MAGENTA 0xF81F
#define YELLOW 0xFFE0
#define WHITE 0xFFFF
#define DOSEBACKGROUND 0x0455

// WiFi variables
unsigned long currentUploadTime;
unsigned long previousUploadTime;
int passwordLength;
int SSIDLength;
int channelIDLength;
int writeAPILength;
char ssid[20];
char password[20];
char channelID[20]; // = "864288";
char channelAPIkey[20]; // = "37SAHQPEQ7FOBC20";
char server[] = "api.thingspeak.com";
int attempts; // number of connection attempts when device starts up in monitoring mode
WiFiClient client;

Adafruit_ILI9341 tft = Adafruit_ILI9341(TFT_CS, TFT_DC);

const int interruptPin = 5;

long count[61];
long fastCount[6]; // arrays to store running counts
long slowCount[181];
int i = 0;         // array elements
int j = 0;
int k = 0;

int page = 0;

long currentMillis;
long previousMillis;
unsigned long currentMicros;
unsigned long previousMicros;

unsigned long averageCount;
unsigned long currentCount;  // incremented by interrupt
unsigned long previousCount; // to activate buzzer and LED
unsigned long cumulativeCount;
float doseRate;
float totalDose;
char dose[5];
int doseLevel;               // determines home screen warning signs
int previousDoseLevel;

bool ledSwitch = 1;
bool buzzerSwitch = 1;
bool wasTouched;
int integrationMode = 0; // 0 = medium, 1 = fast, 2 == slow;

bool doseUnits = 0; // 0 = Sievert, 1 = Rem
unsigned int alarmThreshold = 5;
unsigned int conversionFactor = 175;

int x, y; // touch points

// Battery indicator variables
int batteryInput;
int batteryPercent;
int batteryMapped = 212;       // pixel location of battery icon
int batteryUpdateCounter = 29;

// EEPROM variables
const int saveUnits = 0;
const int saveAlertThreshold = 1; // Addresses for storing settings data in the EEPROM
const int saveCalibration = 2;
const int saveDeviceMode = 3;
const int saveLoggingMode = 4;
const int saveSSIDLen = 5;
const int savePWLen = 6;
const int saveIDLen = 7;
const int saveAPILen = 8;

// Data Logging variables
int addr = 200;                 // starting address for data logging
char jsonBuffer[14000] = "["; 
char data[14500] = "{\"write_api_key\":\"";
unsigned long currentLogTime;
unsigned long previousLogTime;


// Timed Count Variables:
int interval = 5;
unsigned long intervalMillis;
unsigned long startMillis;
unsigned long elapsedTime;
int progress;
float cpm;
bool completed = 0;
int intervalSize; // stores how many digits are in the interval

// Logging variables
bool isLogging;

bool deviceMode;

// interrupt routine declaration
void ICACHE_RAM_ATTR isr();

unsigned int previousIntMicros;              // timers to limit count increment rate in the ISR

const unsigned char gammaBitmap [] PROGMEM = {
	0x30, 0x00, 0x78, 0x70, 0xe8, 0xe0, 0xc4, 0xe0, 0x84, 0xc0, 0x05, 0xc0, 0x05, 0x80, 0x07, 0x80, 
	0x03, 0x00, 0x07, 0x00, 0x0e, 0x00, 0x0e, 0x00, 0x1e, 0x00, 0x1e, 0x00, 0x1e, 0x00, 0x3e, 0x00, 
	0x1c, 0x00, 0x00, 0x00
};

const unsigned char betaBitmap [] PROGMEM = {
	0x00, 0xc0, 0x00, 0x03, 0xf0, 0x00, 0x07, 0x18, 0x00, 0x06, 0x18, 0x00, 0x0e, 0x18, 0x00, 0x0e, 
	0x18, 0x00, 0x0e, 0xf8, 0x00, 0x0e, 0x1c, 0x00, 0x0e, 0x0c, 0x00, 0x0e, 0x0c, 0x00, 0x0e, 0x0c, 
	0x00, 0x0e, 0x0c, 0x00, 0x0f, 0x1c, 0x00, 0x0f, 0xf8, 0x00, 0x0e, 0x00, 0x00, 0x0e, 0x00, 0x00, 
	0x0c, 0x00, 0x00, 0x00, 0x00, 0x00
};
const unsigned char wifiBitmap [] PROGMEM = {
	0x00, 0x00, 0x00, 0x00, 0x00, 0x00, 0x01, 0xf0, 0x00, 0x0f, 0xfe, 0x00, 0x3f, 0xff, 0x80, 0x78, 
	0x03, 0xc0, 0xe0, 0x00, 0xe0, 0x47, 0xfc, 0x40, 0x0f, 0xfe, 0x00, 0x1c, 0x07, 0x00, 0x08, 0x02, 
	0x00, 0x01, 0xf0, 0x00, 0x03, 0xf8, 0x00, 0x01, 0x10, 0x00, 0x00, 0x40, 0x00, 0x00, 0xe0, 0x00, 
	0x00, 0x40, 0x00, 0x00, 0x00, 0x00, 0x00, 0x00, 0x00
};

const unsigned char settingsBitmap[] PROGMEM = {
    0x00, 0x00, 0x00, 0x00, 0x00, 0x00, 0x00, 0x00, 0x00, 0x00, 0x00, 0x00, 0x00, 0x00, 0x00, 0x00,
    0x00, 0x00, 0x00, 0x00, 0x00, 0x00, 0x00, 0x00, 0x00, 0x00, 0x00, 0x00, 0x00, 0x00, 0x00, 0x00,
    0x00, 0x00, 0x00, 0x00, 0x00, 0x00, 0x00, 0x00, 0x00, 0x00, 0x00, 0x00, 0x00, 0x00, 0x00, 0x00,
    0x00, 0x00, 0x00, 0x00, 0x00, 0x00, 0x00, 0x00, 0x00, 0x00, 0x00, 0x1f, 0x80, 0x00, 0x00, 0x00,
    0x00, 0x00, 0x00, 0x3f, 0xc0, 0x00, 0x00, 0x00, 0x00, 0x00, 0x00, 0x3f, 0xc0, 0x00, 0x00, 0x00,
    0x00, 0x00, 0x00, 0x3f, 0xc0, 0x00, 0x00, 0x00, 0x00, 0x00, 0x00, 0x7f, 0xe0, 0x00, 0x00, 0x00,
    0x00, 0x01, 0xc0, 0x7f, 0xe0, 0x38, 0x00, 0x00, 0x00, 0x03, 0xf0, 0x7f, 0xe0, 0xfc, 0x00, 0x00,
    0x00, 0x07, 0xf9, 0xff, 0xf9, 0xfe, 0x00, 0x00, 0x00, 0x0f, 0xff, 0xff, 0xff, 0xff, 0x00, 0x00,
    0x00, 0x0f, 0xff, 0xff, 0xff, 0xff, 0x00, 0x00, 0x00, 0x0f, 0xff, 0xff, 0xff, 0xff, 0x00, 0x00,
    0x00, 0x07, 0xff, 0xff, 0xff, 0xfe, 0x00, 0x00, 0x00, 0x07, 0xff, 0xff, 0xff, 0xfe, 0x00, 0x00,
    0x00, 0x03, 0xff, 0xff, 0xff, 0xfc, 0x00, 0x00, 0x00, 0x01, 0xff, 0xff, 0xff, 0xf8, 0x00, 0x00,
    0x00, 0x01, 0xff, 0xff, 0xff, 0xf8, 0x00, 0x00, 0x00, 0x03, 0xff, 0xf0, 0x7f, 0xfc, 0x00, 0x00,
    0x00, 0x03, 0xff, 0xc0, 0x3f, 0xfc, 0x00, 0x00, 0x00, 0x1f, 0xff, 0x80, 0x1f, 0xff, 0x80, 0x00,
    0x00, 0xff, 0xff, 0x00, 0x0f, 0xff, 0xf0, 0x00, 0x01, 0xff, 0xff, 0x00, 0x07, 0xff, 0xf8, 0x00,
    0x01, 0xff, 0xfe, 0x00, 0x07, 0xff, 0xf8, 0x00, 0x01, 0xff, 0xfe, 0x00, 0x07, 0xff, 0xf8, 0x00,
    0x01, 0xff, 0xfe, 0x00, 0x07, 0xff, 0xf8, 0x00, 0x01, 0xff, 0xfe, 0x00, 0x07, 0xff, 0xf8, 0x00,
    0x01, 0xff, 0xfe, 0x00, 0x07, 0xff, 0xf8, 0x00, 0x00, 0xff, 0xff, 0x00, 0x0f, 0xff, 0xf0, 0x00,
    0x00, 0x1f, 0xff, 0x80, 0x1f, 0xff, 0x80, 0x00, 0x00, 0x03, 0xff, 0xc0, 0x3f, 0xfc, 0x00, 0x00,
    0x00, 0x03, 0xff, 0xe0, 0x7f, 0xfc, 0x00, 0x00, 0x00, 0x01, 0xff, 0xff, 0xff, 0xf8, 0x00, 0x00,
    0x00, 0x01, 0xff, 0xff, 0xff, 0xf8, 0x00, 0x00, 0x00, 0x03, 0xff, 0xff, 0xff, 0xfc, 0x00, 0x00,
    0x00, 0x07, 0xff, 0xff, 0xff, 0xfe, 0x00, 0x00, 0x00, 0x07, 0xff, 0xff, 0xff, 0xfe, 0x00, 0x00,
    0x00, 0x0f, 0xff, 0xff, 0xff, 0xff, 0x00, 0x00, 0x00, 0x0f, 0xff, 0xff, 0xff, 0xff, 0x00, 0x00,
    0x00, 0x0f, 0xff, 0xff, 0xff, 0xff, 0x00, 0x00, 0x00, 0x07, 0xf9, 0xff, 0xf9, 0xfe, 0x00, 0x00,
    0x00, 0x03, 0xf0, 0x7f, 0xe0, 0xfc, 0x00, 0x00, 0x00, 0x01, 0xc0, 0x7f, 0xe0, 0x38, 0x00, 0x00,
    0x00, 0x00, 0x00, 0x7f, 0xe0, 0x00, 0x00, 0x00, 0x00, 0x00, 0x00, 0x3f, 0xc0, 0x00, 0x00, 0x00,
    0x00, 0x00, 0x00, 0x3f, 0xc0, 0x00, 0x00, 0x00, 0x00, 0x00, 0x00, 0x3f, 0xc0, 0x00, 0x00, 0x00,
    0x00, 0x00, 0x00, 0x1f, 0x80, 0x00, 0x00, 0x00, 0x00, 0x00, 0x00, 0x00, 0x00, 0x00, 0x00, 0x00,
    0x00, 0x00, 0x00, 0x00, 0x00, 0x00, 0x00, 0x00, 0x00, 0x00, 0x00, 0x00, 0x00, 0x00, 0x00, 0x00,
    0x00, 0x00, 0x00, 0x00, 0x00, 0x00, 0x00, 0x00, 0x00, 0x00, 0x00, 0x00, 0x00, 0x00, 0x00, 0x00,
    0x00, 0x00, 0x00, 0x00, 0x00, 0x00, 0x00, 0x00, 0x00, 0x00, 0x00, 0x00, 0x00, 0x00, 0x00, 0x00};

const unsigned char buzzerOnBitmap[] PROGMEM = {
    0x00, 0x00, 0x00, 0x00, 0x00, 0x00, 0x00, 0x00, 0x00, 0x00, 0x00, 0x00, 0x00, 0x00, 0x00, 0x00,
    0x00, 0x00, 0x00, 0x00, 0x00, 0x00, 0x00, 0x00, 0x00, 0x00, 0x00, 0x00, 0x00, 0x00, 0x00, 0x00,
    0x00, 0x00, 0x00, 0x00, 0x00, 0x00, 0x00, 0x00, 0x00, 0x00, 0x00, 0x00, 0x03, 0x80, 0x0c, 0x00,
    0x00, 0x00, 0x07, 0x80, 0x0e, 0x00, 0x00, 0x00, 0x0f, 0x80, 0x0f, 0x00, 0x00, 0x00, 0x1f, 0x80,
    0x07, 0x00, 0x00, 0x00, 0x3f, 0x80, 0xc7, 0x80, 0x00, 0x00, 0xff, 0x80, 0xe3, 0x80, 0x00, 0x01,
    0xff, 0x80, 0xf3, 0xc0, 0x00, 0x03, 0xff, 0x80, 0x71, 0xc0, 0x00, 0x07, 0xff, 0x8c, 0x79, 0xc0,
    0x3f, 0xff, 0xff, 0x9e, 0x38, 0xe0, 0x3f, 0xff, 0xff, 0x8e, 0x38, 0xe0, 0x3f, 0xff, 0xff, 0x8e,
    0x3c, 0xe0, 0x3f, 0xff, 0xff, 0x87, 0x1c, 0xe0, 0x3f, 0xff, 0xff, 0x87, 0x1c, 0x60, 0x3f, 0xff,
    0xff, 0x87, 0x1c, 0x70, 0x3f, 0xff, 0xff, 0x87, 0x1c, 0x70, 0x3f, 0xff, 0xff, 0x87, 0x1c, 0x70,
    0x3f, 0xff, 0xff, 0x87, 0x1c, 0x70, 0x3f, 0xff, 0xff, 0x87, 0x1c, 0x70, 0x3f, 0xff, 0xff, 0x87,
    0x1c, 0xe0, 0x3f, 0xff, 0xff, 0x8e, 0x3c, 0xe0, 0x3f, 0xff, 0xff, 0x8e, 0x38, 0xe0, 0x3f, 0xff,
    0xff, 0x9e, 0x38, 0xe0, 0x00, 0x07, 0xff, 0x8c, 0x79, 0xc0, 0x00, 0x03, 0xff, 0x80, 0x71, 0xc0,
    0x00, 0x00, 0xff, 0x80, 0xf1, 0xc0, 0x00, 0x00, 0x7f, 0x80, 0xe3, 0x80, 0x00, 0x00, 0x3f, 0x80,
    0xc7, 0x80, 0x00, 0x00, 0x1f, 0x80, 0x07, 0x00, 0x00, 0x00, 0x0f, 0x80, 0x0f, 0x00, 0x00, 0x00,
    0x07, 0x80, 0x0e, 0x00, 0x00, 0x00, 0x03, 0x80, 0x0c, 0x00, 0x00, 0x00, 0x00, 0x00, 0x00, 0x00,
    0x00, 0x00, 0x00, 0x00, 0x00, 0x00, 0x00, 0x00, 0x00, 0x00, 0x00, 0x00, 0x00, 0x00, 0x00, 0x00,
    0x00, 0x00, 0x00, 0x00, 0x00, 0x00, 0x00, 0x00, 0x00, 0x00, 0x00, 0x00, 0x00, 0x00};

const unsigned char buzzerOffBitmap[] PROGMEM = {
    0x00, 0x00, 0x00, 0x00, 0x00, 0x00, 0x00, 0x00, 0x00, 0x00, 0x00, 0x00, 0x00, 0x00, 0x03, 0x80,
    0x00, 0x00, 0x00, 0x00, 0x0f, 0x80, 0x00, 0x00, 0x00, 0x00, 0x1f, 0x80, 0x00, 0x00, 0x00, 0x00,
    0x3f, 0x80, 0x00, 0x00, 0x00, 0x00, 0x7f, 0x80, 0x00, 0x00, 0x00, 0x00, 0xff, 0x80, 0x00, 0x00,
    0x00, 0x03, 0xff, 0x80, 0x00, 0x00, 0x00, 0x07, 0xff, 0x80, 0x00, 0x00, 0x00, 0x0f, 0xff, 0x80,
    0x00, 0x00, 0x0f, 0xff, 0xff, 0x80, 0x00, 0x00, 0x1f, 0xff, 0xff, 0x80, 0x00, 0x00, 0x3f, 0xff,
    0xff, 0x8f, 0x00, 0x78, 0x7f, 0xff, 0xff, 0x8f, 0x80, 0xf8, 0x7f, 0xff, 0xff, 0x8f, 0xc1, 0xf8,
    0x7f, 0xff, 0xff, 0x87, 0xe3, 0xf0, 0x7f, 0xff, 0xff, 0x83, 0xf7, 0xe0, 0x7f, 0xff, 0xff, 0x81,
    0xff, 0xc0, 0x7f, 0xff, 0xff, 0x80, 0xff, 0x80, 0x7f, 0xff, 0xff, 0x80, 0x7f, 0x00, 0x7f, 0xff,
    0xff, 0x80, 0x7f, 0x00, 0x7f, 0xff, 0xff, 0x80, 0xff, 0x80, 0x7f, 0xff, 0xff, 0x81, 0xff, 0xc0,
    0x7f, 0xff, 0xff, 0x83, 0xf7, 0xe0, 0x7f, 0xff, 0xff, 0x87, 0xe3, 0xf0, 0x7f, 0xff, 0xff, 0x8f,
    0xc1, 0xf0, 0x7f, 0xff, 0xff, 0x8f, 0x80, 0xf8, 0x3f, 0xff, 0xff, 0x8f, 0x00, 0x70, 0x3f, 0xff,
    0xff, 0x84, 0x00, 0x20, 0x1f, 0xff, 0xff, 0x80, 0x00, 0x00, 0x0f, 0xff, 0xff, 0x80, 0x00, 0x00,
    0x00, 0x07, 0xff, 0x80, 0x00, 0x00, 0x00, 0x03, 0xff, 0x80, 0x00, 0x00, 0x00, 0x01, 0xff, 0x80,
    0x00, 0x00, 0x00, 0x00, 0xff, 0x80, 0x00, 0x00, 0x00, 0x00, 0x7f, 0x80, 0x00, 0x00, 0x00, 0x00,
    0x1f, 0x80, 0x00, 0x00, 0x00, 0x00, 0x0f, 0x80, 0x00, 0x00, 0x00, 0x00, 0x07, 0x80, 0x00, 0x00,
    0x00, 0x00, 0x03, 0x80, 0x00, 0x00, 0x00, 0x00, 0x00, 0x00, 0x00, 0x00, 0x00, 0x00, 0x00, 0x00,
    0x00, 0x00, 0x00, 0x00, 0x00, 0x00, 0x00, 0x00, 0x00, 0x00, 0x00, 0x00, 0x00, 0x00};
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

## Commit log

2019-09-21 Addel Gerbers, Schematic, Solidworks and STL files
    [Case main.STL, Cover.STL]
2019-10-01 Added order list
    [LCSC Order list.xlsx]
2019-10-04 Fixed battery level constants
2019-10-04 Fixed battery level input range
2019-10-04 Updated Order list
    [LCSC Order list.xlsx]
